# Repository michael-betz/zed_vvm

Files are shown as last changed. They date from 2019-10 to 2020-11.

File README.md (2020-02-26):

# zed_vvm
A digital RF vector volt-meter (VVM).
Measures amplitude and phase of a sinusoidal signal under test against a reference signal of same frequency.
Intended as an instrument to monitor and troubleshoot legacy accelerator RF systems.

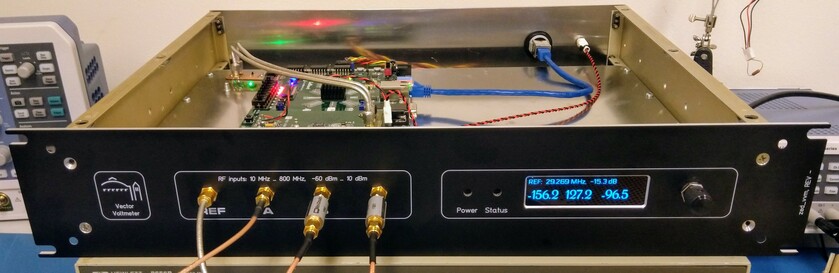
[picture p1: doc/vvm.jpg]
Photo of first prototype chassis


Based on a Digilent Zedboard running Debian with a DC1525A FMC daughter board on top.

  * 4 channel, 14 bit, 125 MSps, 800 MHz bandwidth (3 dB) analog to digital converter with LVDS interface: [__LTC2175-14__](https://www.analog.com/en/products/ltc2175-14.html)
  * Sampling clock provided by a `Si5xx-PROG_EVB` evaluation board running [custom firmware](https://github.com/yetifrisstlama/Si5xx-5x7-EVV_autoloader)
  * 4 x 4096 sample buffer with oscilloscope-like trigger for raw ADC waveform storage (`scope_app.py` makes use of that)
  * FPGA implements
    * digital down-conversion and decimation to get a complex baseband (IQ) signal
    * rectangular (IQ) to polar conversion (magnitude, phase)
    * first order IIR filter to smooth the measurement result
    * uses [Bedrock](https://github.com/BerkeleyLab/Bedrock) DSP blocks
    * makes good use of [litex](https://github.com/enjoy-digital/litex) Control/Status Registers (CSRs), the wishbone2axi bridge and litex_server to make the measurements available to linux running on the CPU

The main reason to choose embedded linux is the convenience for application development:
  * python3 support with numpy / scipy or even jupyter notebook
  * `sudo apt install <whatever_you_need>`
  * ssh and scp make remote access secure and easy, even on the public internet
  * remote loading of bit-files through scp is very convenient
  * litex_server can run on the zedboard, making access to CSR-registers over
    ethernet easy and transparent. The TCP connection is tunneled trough ssh,
    making it secure
  * can run epics IOC, mosquitto client or many other tools to publish
    measurement results

# Minimum design goals
  * support 125 MHz & 500 MHz signals
  * Same phase reading after power cycle (manage clock divider states)
  * 360 degree unique measurement range
  * Phase accuracy over a temperature range of 20 - 30 degC of better than 1 deg (0.2 %)
  * Less than 2 % amplitude error
  * At least 2 input channels + one phase reference channel
  * Self-contained instrument (only power is needed)
  * Easy to use
  * Not too expensive, such that it can be installed in multiple places across the facility
  * Epics support

# System block diagram
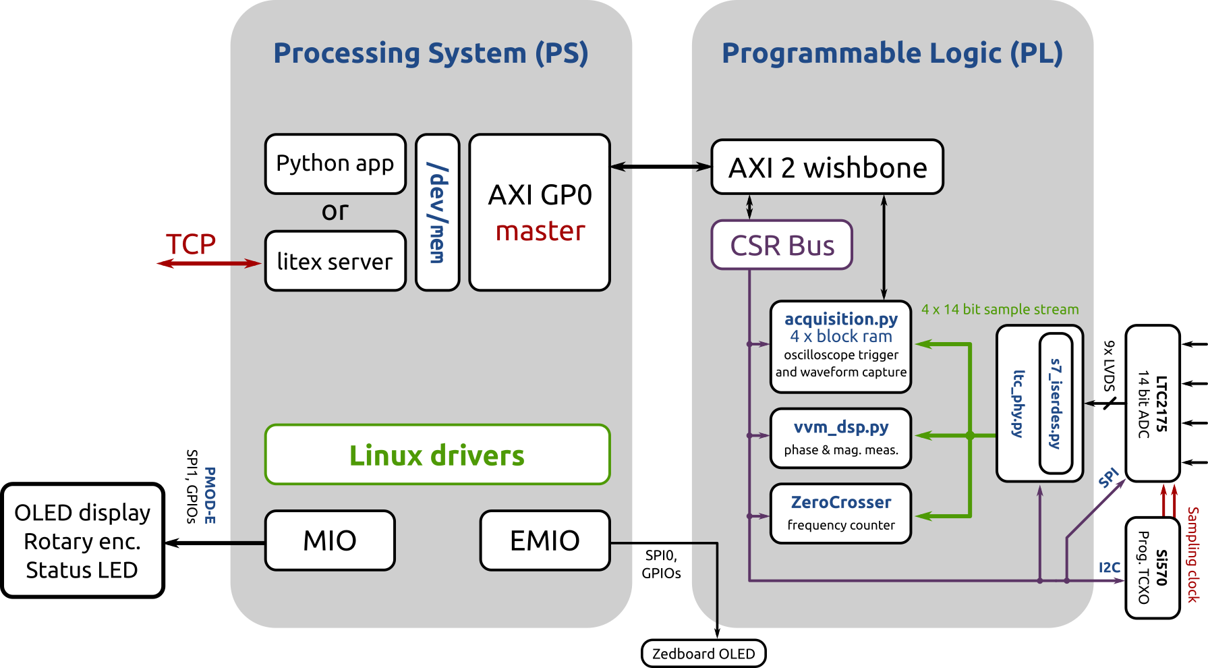
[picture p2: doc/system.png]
High level system overview


# `vvm_dsp.py` block diagram
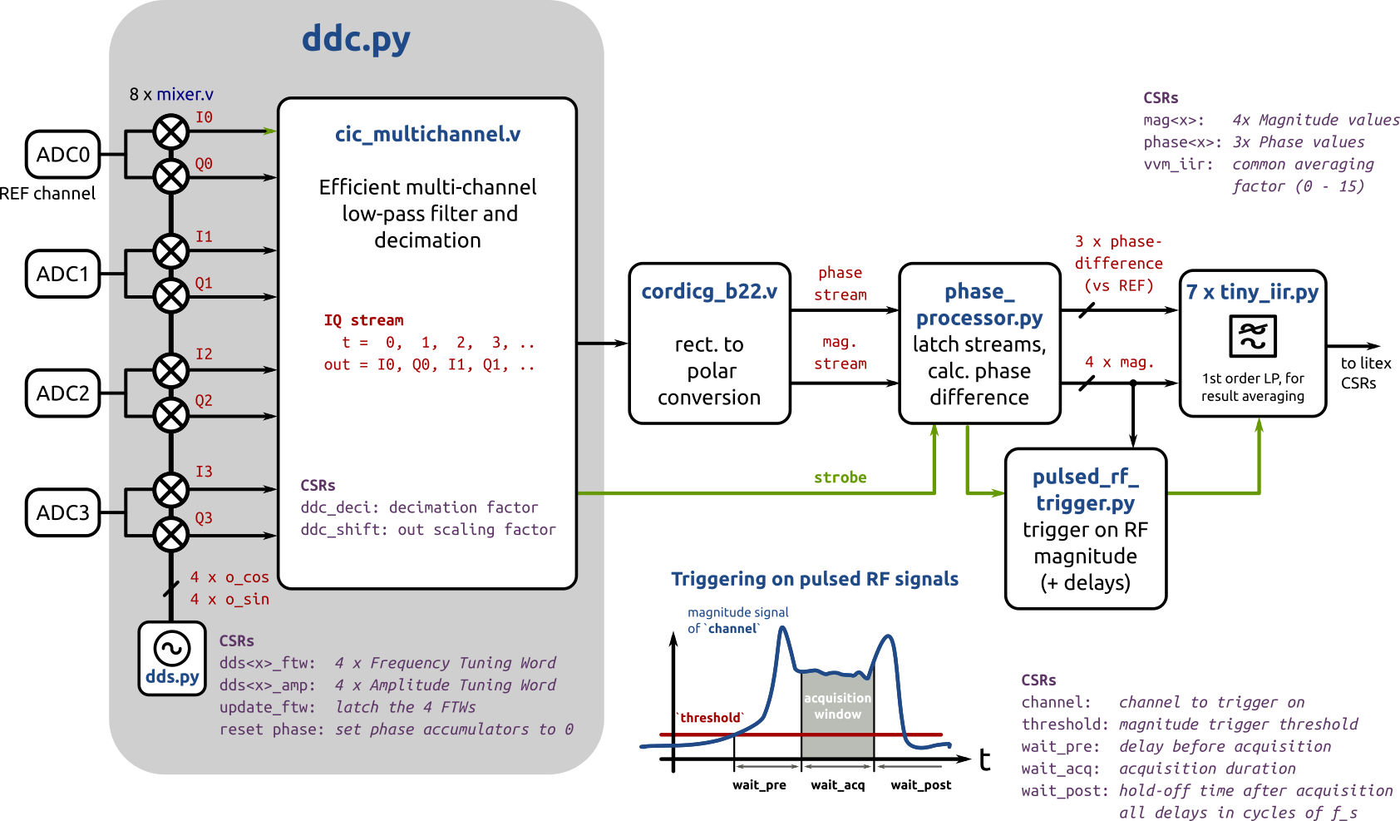
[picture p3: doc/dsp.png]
DSP blocks implementing the VVM


# `phase_processor.py` block diagram
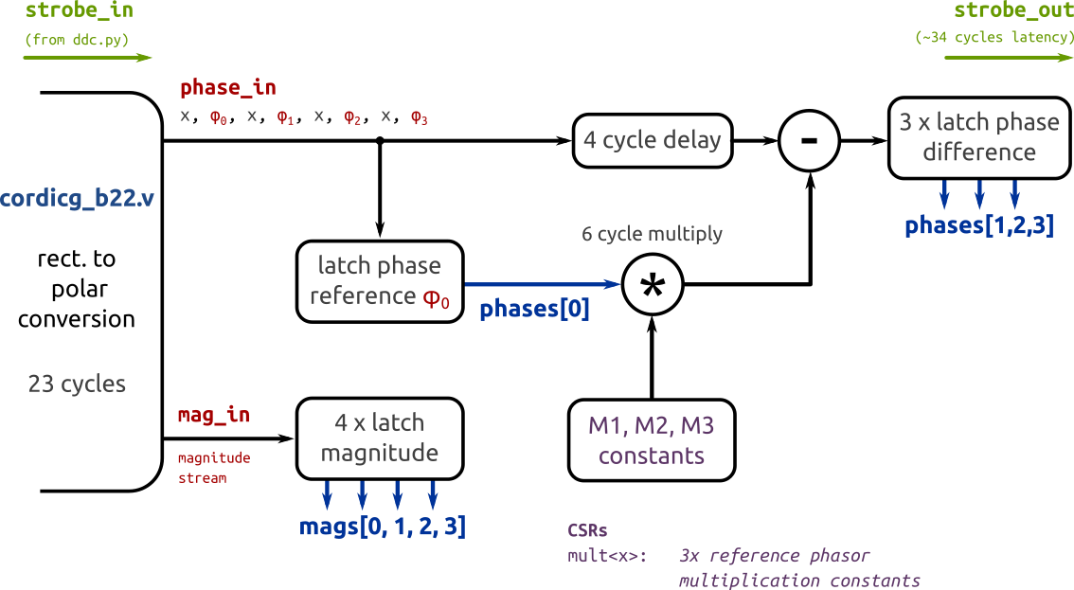
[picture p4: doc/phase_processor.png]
Phase and Magnitude pipelined data path


# Hardware modifications
## Zedboard
  * remove XADC header (J2) as it interferes with the DC1525A board

## DC1525A
  * Setup the board for differential sample clock input
    * Move R101 to R64 (0 Ohm jumper)
  * Remove low-pass filter on the analog input channels
    * Remove: R37, R38, R53, R54, R80, R81, R90, R91
    * Remove: R35, R52, R79, R89
    * Replace by 0 Ohm jumper: L4, L5, L6, L12

# Installing litex
... on debian
```bash
$ sudo apt install libevent-dev libjson-c-dev
$ sudo pip3 install virtualenvwrapper
$ mkvirtualenv litex
$ git clone git@github.com:yetifrisstlama/litex.git --recursive
$ cd litex
$ python litex_setup.py init
$ python litex_setup.py install
$ python setup.py develop
```

# Building the .bit file
Most of the DSP blocks are from LBLs `Bedrock` repo, which needs to be cloned
in the same directory as `zed_vvm`.

Vivado needs to be installed an in the PATH. I use v2019.1.

Setup your zedboard host-name in `util/remote_config_fpga.sh` and
`util/remote_litex_server.sh`.

Note that the Zedboard PS will freeze if the FPGA is not loaded / in the process of being loaded and there is a
AXI memory access through litex_server. So make sure to close the python apps before doing `make upload`.

```bash
$ git clone https://github.com/yetifrisstlama/zed_vvm.git
$ git clone https://github.com/BerkeleyLab/Bedrock.git
$ cd zed_vvm/gateware
$ workon litex
$ make
# remote FPGA configuration
$ make upload
# start litex_server on zedboard for remote access to FPGA registers
$ make server
# Keep this terminal open and start a new one
```

# Demo apps
[litex_server_apps](litex_server_apps/README.md)

# Setting up linux
[ZED_DEBIAN.md](linux_kernel/ZED_DEBIAN.md)

# Setting up Peripherals
How to connect Linux to the FPGA or the outside world. WIP ...

[PS_PERIPHERALS.md](linux_kernel/PS_PERIPHERALS.md)

# Load bitfile in linux
Bitfiles are loaded trough the [Linux FPGA Manager](https://www.kernel.org/doc/html/v4.18/driver-api/fpga/fpga-mgr.html).
For this to work, the .bit file needs its header removed and its bytes swapped.
This can either be done with the xilinx SDK or alternatively with `bitstream_fix.py`.
```bash
python3 util/bitstream_fix.py <bitfile>.bit
```

copy the resulting `<bitfile>.bit.bin` on the zedboard, then

```bash
    sudo -i
    cp <bitfile>.bit.bin /lib/firmware/
    echo 0 > /sys/class/fpga_manager/fpga0/flags
    echo <bitfile>.bit.bin > /sys/class/fpga_manager/fpga0/firmware
    dmesg

[ 1667.020520] fpga_manager fpga0: writing <bitfile>.bit.bin to Xilinx Zynq FPGA Manager
```

`cd gateware; make upload` tries to automate all these steps.

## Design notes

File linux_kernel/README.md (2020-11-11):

# linux_kernel

__.config__ my current mainline linux kernel configuration file for `make menuconfig`.
Copy / link it to `linux/.config`.

__zynq-zed.dts__ my current device tree.
Copy / link it to `linux/arch/arm/boot/dts/zynq-zed.dts`.

__fpga-mgr.patch__ Patch for the linux mainline kernel to get the /sys/class/fpga_mgr/fpga0/firmware file which is needed to easily configure the fpga from linux. The xilinx version of the kernel has this little convenience feature already builtin.

__ZED_DEBIAN.md__ Instructions on how to get a useful version of linux running on the zedboard.

__EPICS.md__ How to use `qemu` and `chroot` to cross-compile EPICS and an IOC and run it on the zedboard

__PS_PERIPHERALS.md__ Notes on how zynq peripherals are integrated into linux.

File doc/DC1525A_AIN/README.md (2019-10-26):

# LT spice simulation
... of the DC1525A analog input circuit.
It's a low-pass filter with corner frequency of ~ 100 MHz, made up of
discreet components.

As we want to measure 500 MHz signals, the low-pass needs to be removed.

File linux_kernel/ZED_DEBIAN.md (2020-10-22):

# Steps to get debian running on zedboard
It's like having a raspberry pi in your FPGA :)

This guide is mostly based on these two:
  * https://github.com/PyHDI/zynq-linux
  * https://blog.n621.de/2016/05/running-linux-on-a-zynq-without-vivado-madness/

## Bootloader
The stock version of U-Boot works perfectly fine for the Zynq7000 on the zedboard. No need for the Xilinx version.
```bash
# Cross compiler
    sudo apt install libc6-armel-cross libc6-dev-armel-cross binutils-arm-linux-gnueabi libncurses-dev
    sudo apt-get install gcc-arm-linux-gnueabi g++-arm-linux-gnueabi libssl-dev
    export CROSS_COMPILE=arm-linux-gnueabi-
    export ARCH=arm

# compile U-Boot
    git clone https://github.com/u-boot/u-boot.git
    cd u-boot/
    git checkout 0f3e2942c9e01b5dfc01f3dabe0e2f2ab8fd8b84
    export DEVICE_TREE=zynq-zed  # for zedboard
    make xilinx_zynq_virt_defconfig
    make menuconfig

# We want u-boot to read uEnv.txt from SD-card to setup its environment.
# Tick `Enable a default value for bootcmd`
# ... for `bootcmd value` enter the line below:
fatload mmc 0 0x10000 uEnv.txt;env import -t 0x10000 $filesize;boot

# Optional, apply a customized Zynq PS configuration on startup:
# under ARM architecture --> Zynq/ZynqMP PS init file(s) location
# enter:
<path to zed_vvm>/gateware/ip/ps7_init_gpl.c
# see also: `PS_PERIPHERALS.md`

    make

    # `mkimage` will be needed for building the kernel
    export PATH=$PATH:<..>/u-boot/tools/

# Create a ~ 64 MB FAT32 partition on the SD card,
# follow the guide below or use gparted
# in this example it's mounted as /media/sdcard

# Copy first stage bootloader and u-boot image to SD card
    cp spl/boot.bin /media/sdcard
    cp u-boot.img /media/sdcard

# Now try it on the Zedboard, you should see u-boot starting on the UART
```
### Erasing the flash
There's a caveat here. U-Boot can store its environment in the SPI flash, which will override the default $bootcmd we set up in menuconfig. To fix this, erase the flash from within the u-boot shell:

```bash
# This is a sign that uEnv.txt was not loaded correctly from MMC
Zynq> echo $bootcmd
run $modeboot

# Flash needs to be erased ...
Zynq> sf probe
Zynq> sf erase 0 0x2000000
Zynq> reset

# Now it looks good:
Zynq> echo $bootcmd
run kernel_load; run dtr_load; setenv ethaddr 00:0a:35:00:01:87; run kernel_boot
```

### bootstrapping u-boot over JTAG
... with openocd
```tcl
reset halt
load_image u-boot/spl/u-boot-spl.bin 0
resume 0
sleep 1000
halt
load_image u-boot/u-boot.bin 0x4000000
resume 0x4000000
```

### Installing u-boot to flash
https://xilinx-wiki.atlassian.net/wiki/spaces/A/pages/18842574/U-Boot+Secondary+Program+Loader

## Linux kernel
The [vanilla mainline kernel](https://github.com/torvalds/linux) works perfectly fine on the zedboard for this application (see note below).
Here's instructions on how to apply two tiny patches to enable FPGA configuration from the command line and OLED support. If you go with the Xilinx version of the kernel, you don't need the two patches, but most of the instructions below still apply.

```bash
    git clone https://github.com/torvalds/linux.git
    cd linux/
    git checkout 22fbc037cd32e4e6771d2271b565806cfb8c134c

# Load my kernel config and device tree for zed_vvm
    cp <..>/zed_vvm/linux_kernel/zedboard_defconfig arch/arm/configs/
    cp <..>/zed_vvm/linux_kernel/zynq-zed.dts arch/arm/boot/dts/

# Patch to get /sys/class/fpga_mgr/fpga0/firmware
# Not needed with the xilinx version of the kernel
    patch --strip=1 --input=<..>/zed_vvm/linux_kernel/fpga-mgr.patch

# If you want to use the tiny ssd1306 based display on the zed-board,
# replace the kernel fbtft driver with a working version:
    cd drivers/staging
    rm -rf fbtft
    git clone https://github.com/yetifrisstlama/fbtft.git

# Apply any kernel customization you might need
    cd ../..
    export CROSS_COMPILE=arm-linux-gnueabi- ARCH=arm
    make zedboard_defconfig
    make menuconfig
    # make sure the display drivers are all enabled under
    # Device Drivers --> Staging drivers --> Support for small TFT LCD display modules
```

Then build the kernel and device-tree ...

```bash
    make -j4 uImage LOADADDR=0x00008000
    # good time to get a cup of coffee
    make zynq-zed.dtb
```

copy kernel image and device-tree to SD card

```bash
    cp arch/arm/boot/uImage /media/sdcard/
# for zedboard
    cp arch/arm/boot/dts/zynq-zed.dtb /media/sdcard
# for microzed
    cp arch/arm/boot/dts/zynq-microzed.dtb /media/sdcard
```

to configure u-boot, create a `uEnv.txt` as shown below and copy it to SD card.

SD card contents should look like this now:
```bash
ls -hl /media/<..>
total 5.6M
-rw-r--r-- 1 michael michael 117K Oct  3 19:42 boot.bin
-rw-r--r-- 1 michael michael 1.1M Oct  3 19:42 u-boot.img
-rw-r--r-- 1 michael michael  735 Oct  3 19:42 uEnv.txt
-rw-r--r-- 1 michael michael 4.4M Oct  3 19:43 uImage
-rw-r--r-- 1 michael michael  12K Oct  3 19:43 zynq-zed.dtb
```
Now is a good time to give it a test-run on the Zedboard,
the linux kernel should boot and panic because of the missing root filesystem

## Mainline kernel
Pros of going mainline
  * more widely adopted
  * hence better peer-reviewed

The Zynq7000 is pretty well supported now in the mainline kernel.

[Mainline vs. Xilinx Kernel](https://xilinx-wiki.atlassian.net/wiki/spaces/A/pages/18841873/Linux+Drivers)

I started this project on the Xilinx kernel-fork. When I first tried switching over to mainline, I just copied `linux-xlnx/.config` to `linux/.config` and compiled as of the instructions above.

  * Both OLED displays, GPIOs and rotary encoder worked as expected
  * It booted without errors in dmesg
  * `/sys/class/fpga_manager/fpga0` was there, so the linux FPGA manager driver was working

However I was missing `/sys/class/fpga_manager/fpga0/firmware`,
which is used to pipe the name of a `.bit.bin` file to re-program the FPGA PL from linux. After some investigation, it looks like the fpga-manager was not intended to be accessed from user-space and Xilinx added this feature as a convenience for developers. I brought it back with a [tiny patch](fpga-mgr.patch) to the mainline kernel.

With the patch I was able to load bit-files in the same way as with the
 Xilinx kernel. However the fabric clocks were still disabled and the FPGA
 appeared completely un-responsive after configuration.
 Some intensive diff-ing later I could trace this down to different default settings in `zynq-7000.dtsi`.
 Switching the clocks back on was easily done in [`zynq-zed.dts`](zynq-zed.dts)
 and life on mainline is good now.

## Debian buster rootfs

### Shortcut: install pre-made rootfs
This assumes `/dev/mmcblk0p2` is the large ext4 partition on the SD card/.
```bash
    wget https://github.com/yetifrisstlama/zed_vvm/releases/download/v0.1/rootfs_buster_clean.tar.gz
    sudo mkfs.ext4 -v /dev/mmcblk0p2 -L rootfs
    # Mount the partition (easiest in gui file manger)
    cd /media/<..>/rootfs
    sudo tar -xzvf <..>/rootfs_buster_clean.tar.gz
    sync
```

Put the SD-card in the zedboard, connect to its UART and
watch it booting into debian. There should be a login prompt on the UART.

__If you've downloaded `rootfs_buster_clean.tar.gz` change the passwords !!!__
login as each of the two users below and run the `passwd` command.

```bash
    #user: root, default pw: root
    #user: zed, default pw: zed
```

Also remote login over ssh should work now if the network is up.

The last step (if ssh works) is to copy the `linux_apps` directory
form the host machine onto the zedboard:

```bash
    scp -r <..>/zed_vvm/linux_apps <user_name>@<hostname>:~
```

Alternatively, just install my [litex-fork](https://github.com/yetifrisstlama/litex) on the zedboard, which includes
litex_server with mmap access support.

### Debian certificate troubles
I forgot to include openssl in `rootfs_buster_clean.tar.gz`. So `sudo apt update` may refuse to work and complain about missing certificates. I fixed this by downloading on my host machine:

  * [openssl-armhf](https://packages.debian.org/buster/openssl)
  * [ca-certificates](https://packages.debian.org/buster/ca-certificates)

copying them on the zeboard with `scp` and installing them with `sudo apt install ./<file_name>`.

### Taking the scenic route ...
setup your initial bare-bones debian environment using chroot on a debian based linux host PC.

```bash
# debian rootfs (on host)
    sudo apt install debootstrap qemu-user-static
    mkdir rootfs
    sudo debootstrap --arch=armhf --foreign buster rootfs
    sudo cp /usr/bin/qemu-arm-static rootfs/usr/bin/
    sudo chroot rootfs/

# debian rootfs (chroot)
    distro=buster
    export LANG=C
    debootstrap/debootstrap --second-stage
    nano /etc/apt/sources.list

deb http://deb.debian.org/debian buster main
deb http://deb.debian.org/debian-security/ buster/updates main
deb http://deb.debian.org/debian buster-updates main

    apt update
    apt upgrade
    apt install locales sudo ntp openssh-server python3

    # Enable `en_US.UTF-8` and set it as default locale
    dpkg-reconfigure locales

    # Set root password
    passwd

    # Add a user with sudo permissions
    adduser <user_name>
    visudo

root        ALL=(ALL:ALL) ALL
<user_name> ALL=(ALL:ALL) NOPASSWD: ALL
# Note: the `NOPASSWD: ` flag means sudo will not ask for a password.
# convenient for development but dangerous. Don't do this in production!

    # Enable DHCP
    nano /etc/network/interfaces

allow-hotplug eth0
iface eth0 inet dhcp

    # Set hostname
    nano /etc/hostname

<hostname>

    nano /etc/hosts

127.0.0.1   localhost <hostname>
::1     localhost ip6-localhost ip6-loopback
ff02::1     ip6-allnodes
ff02::2     ip6-allrouters

# Mount the fat16 boot partition
# This is useful for remote updates of
#   * first stage boot-loader (boot.bin)
#   * u-boot.img
#   * device tree (.dts)
#   * kernel image (uImage)
#   * u-boot config (uEnv.txt)
    mkdir /boot  # only if it does not exist already
    nano /etc/fstab

/dev/mmcblk0p1 /boot auto defaults 0 0

# For remote fpga loading
    mkdir /lib/firmware

# Optional Hacks
# get cross-compiled binaries to run
# otherwise I get `bash: ./hw: No such file or directory`
    sudo ln -s /lib/arm-linux-gnueabihf/ld-2.28.so /lib/ld-linux.so.3

# to prevent sshd taking forever to start after reboot and
# `random: 7 urandom warning(s) missed due to ratelimiting`
    sudo apt install haveged

# ------------------------
#  Exit the chroot shell
# ------------------------

# Archive rootfs in a .tar.gz file
    cd rootfs
    sudo tar -cpzvf ../rootfs_buster_clean.tar.gz .
```

Un-tar the rootfs onto a large ext4 partition on the SD card as shown [here](ZED_DEBIAN.md#shortcut-install-pre-made-rootfs).

## Partitioning the SD card
What we need

  * FAT16 partition of size 32 MB
  * Linux (ext4) over the remaining available space

Using `fdisk` on a 2 GB SD card, it should look like this:

```
Device         Boot Start     End Sectors  Size Id Type
/dev/mmcblk0p1       2048   67583   65536   32M  e W95 FAT16
/dev/mmcblk0p2      67584 3842047 3774464  1.8G 83 Linux
```

then format the partitions as FAT16 and ext4

```bash
sudo mkfs.vfat -F16 -v /dev/mmcblk0p1 -n boot
sudo mkfs.ext4 -v /dev/mmcblk0p2 -L rootfs
```

__make sure to replace `mmcblk0p1` and `mmcblk0p2` with the actual partition names__

# uEnv.txt
U-Boot startup script to boot and optionally load a bitfile. Make sure `ethaddr` is unique on network.
```bash
# I get corrupt data from MMC if the caches are enabled :(
init=icache off; dcache off

fpga_addr=0x10000000
fpga_load=load mmc 0 ${fpga_addr} zed_wrapper.bit.bin
fpga_boot=fpga load 0 ${fpga_addr} $filesize

kernel_addr=0x8000
kernel_load=load mmc 0 ${kernel_addr} uImage

dtr_addr=0x100
dtr_load=load mmc 0 ${dtr_addr} zynq-zed.dtb

kernel_boot=setenv bootargs console=ttyPS0,115200 root=/dev/mmcblk0p2 rw rootwait; bootm ${kernel_addr} - ${dtr_addr}

# Boot from MMC without loading a bit-file, make sure to change ethaddr to a random value
bootcmd=run init; run kernel_load; run dtr_load; setenv ethaddr 00:0a:35:00:42:87; run kernel_boot

# Load a bit-file and boot from MMC, make sure .bit.bin file from line 2 exists
# bootcmd=run init; run fpga_load; run fpga_boot; run kernel_load; run dtr_load; setenv ethaddr 00:0a:35:00:42:87; run kernel_boot

# network boot: load uImage and zynq-zed.dtb over tftp and boot it
# ipaddr=192.168.1.2
# serverip=192.168.1.1
# netmask=255.255.255.0
# bootcmd=run init; tftpboot $kernel_addr uImage; tftpboot $dtr_addr zynq-zed.dtb; run kernel_boot
```

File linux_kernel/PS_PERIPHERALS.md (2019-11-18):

# PS7 peripherals configuration
The Zynq Processing System (PS) is the CPU part of the FPGA. It has several peripherals like SPI, CAN, I2C, UART, GPIO, etc. These are connected to dedicated IO pins on the chip (MIO) or to the FPGA Programmable Logic (EMIO), from where they can be routed to any other IO pin of the chip through the FPGA fabric. Configuration happens in Vivado through the `ZYNQ7 Processing system` IP block.

If the PS7 block is not included in the PL design, the CPU will freeze as soon as the the resulting bitfile is loaded. The PL part of the design will work as intended, even without the PS7 block.

Configuration of the PS7 block is stored in the Xilinx IP file `ip/processing_system7_0.xci`, which is required by the Litex `SoCZynq()` class.

To manually generate this file, follow these steps:

  1. open Vivado, new RTL project, `zedboard` hardware platform, don't add source files, next, next next ..
  2. IP Integrator --> Create Block Design
  3. Add `ZYNQ7 Processing system` IP
  4. Run vivado design automation to get default values for Zedboard
  5. Configure the PS7 block in GUI
       * Bank0 / 1 voltage = 2.5 V
       * Clock Configuration, PL Fabric Clocks: clock0 100 MHz. The litex `sysclk` domain is driven by clock0
  6. Peripheral I/O Pins
       * The PS_MIOX pins are connected to the PS and can be configured here for special function operation (like CAN, I2C, SPI, UART, GPIO)
       * PMOD JE1 is exclusively connected to MIOs (see table below). This might be useful to drive a small graphical LCD from linux trough an SPI interface
  7. Save and close, this generates the file `<name>.srcs/sources_1/ip/processing_system7_0/processing_system7_0.xci` in the project directory, which needs to be copied to `./ip`

__All these steps have now been automated by `ip/gen_ip.tcl`.__

This .tcl script is automatically run by the Makefile. If you want to change the PS configuration, change only this file.

## Peripherals connected to PS

These are accessible from linux when configured in step 6 above (most are already configured by default) and once the right driver has been loaded, which requires an entry into the linux device tree.

| Net      |PS_EMIO<x> |              |
| -------- | --------- | ------------ |
|__PMOD-A__|           | __FP PCB__   |
|  JA1     | 54        | ENCODER: B   |
|  JA2     | 55        | ENCODER: SW  |
|  JA3     | 56        | ENCODER: A   |
|  JA4     | 57        | STATUS_LED   |
| JA10     |           | OLED: MOSI   |
|  JA9     |           | OLED: SCLK   |
|  JA8     |           | OLED: /CS    |
|  JA7     | 58        | OLED: D/C    |
|__PMOD-B__|           |__Si570 PCB__ |
|  JB1     |           |              |
|  JB2     |           |              |
|  JB3     |           |              |
|  JB4     |           |              |
| JB10     |           | SDA          |
|  JB9     |           | SCL          |
|  JB8     |           | OE           |
|  JB7     |           | NC           |

### PMOD-E is dedicated to the PS-wired MIO pins
Will be used with the front panel PCB for the user interface.

| Net      | PS_MIO<x> | PS7, SPI1  |              |
| -------- | --------- | ---------- | ------------ |
|__PMOD-E__|           |            | __FP PCB__   |
|  JE1     | 13        | SS[0]      | OLED: /CS    |
|  JE2     | 10        | MOSI       | OLED: MOSI   |
|  JE3     | 11        | MISO       | ENCODER: SW  |
|  JE4     | 12        | SCLK       | OLED: SCLK   |
| JE10     | 15        | SS[2]      | OLED: D/C    |
|  JE9     | 14        | SS[1]      | STATUS_LED   |
|  JE8     | 9         |            | ENCODER: B   |
|  JE7     | 0         |            | ENCODER: A   |
|__Button__|           |            |              |
|  PB1     | 50        |            |              |
|  PB2     | 51        |            |              |
| __LED__  |           |            |              |
|  LD9     |7 (USB rst)|            |              |

Note on PS7:
  * MIO0 - MIO53
  * EMIO54 - EMIO117

Change MIO11 from MISO to GPIO with pullup in `ps7_init_gpl.c`.
The Vivado GUI does not allow this configuration, that's why we have
to hack it.

```
    from: EMIT_MASKWRITE(0XF800072C, 0x00003FFFU ,0x000007A0U),
    to:   EMIT_MASKWRITE(0XF800072C, 0x00003FFFU ,0x00001600U)
```
this has been automated in the Makefile

# Zedboard OLED
TODO: add guide to get FBTFT running

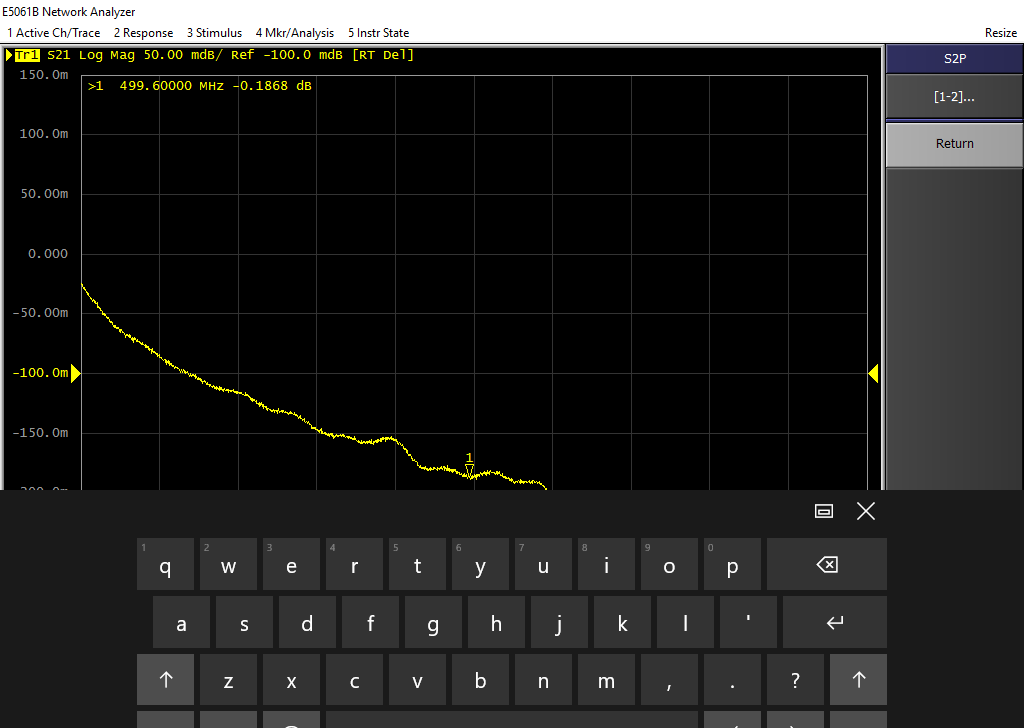
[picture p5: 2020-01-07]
litex_server_apps/cal/vna/CAB.PNG

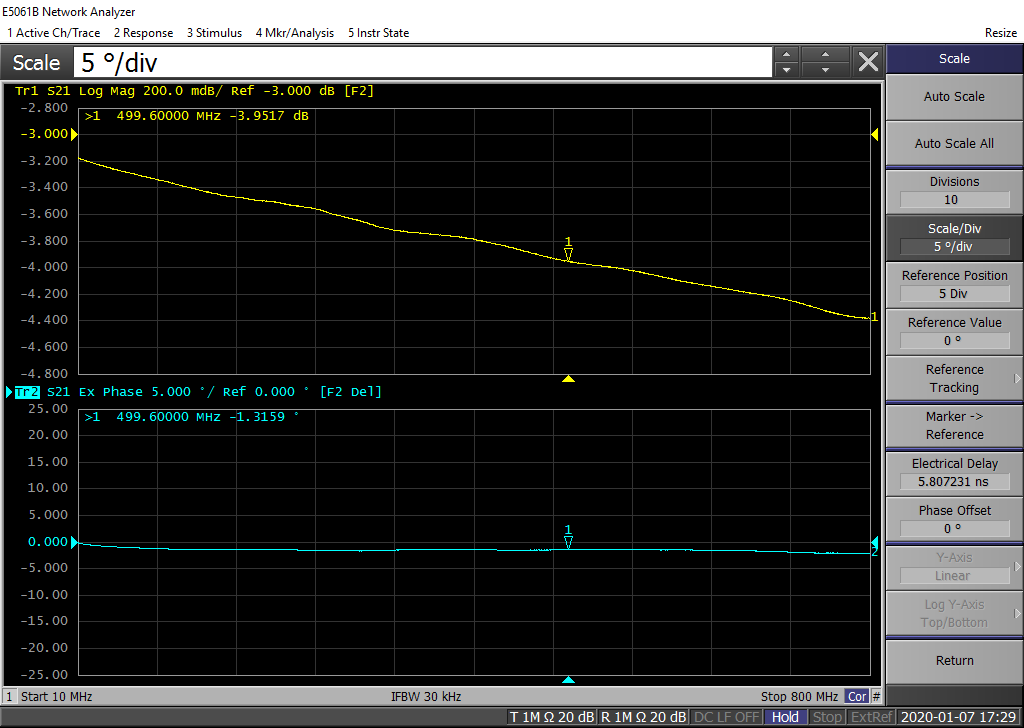
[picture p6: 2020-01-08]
litex_server_apps/cal/vna/PDIV_CH1.PNG

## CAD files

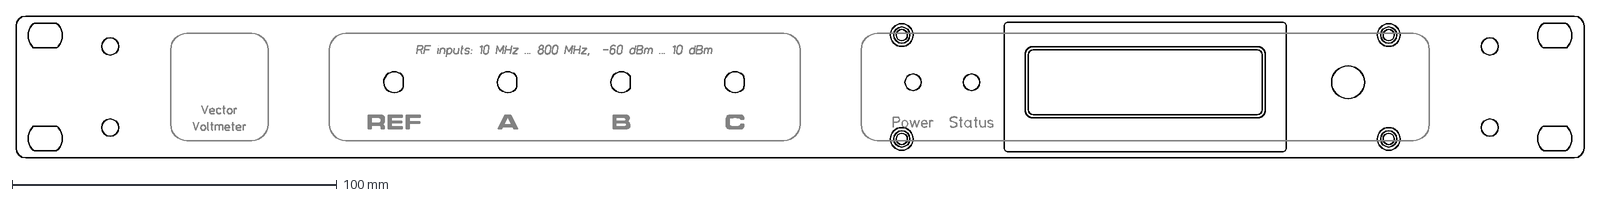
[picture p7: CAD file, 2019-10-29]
pcb/frontpanel/vvm.dxf
483.0 x 43.6 mm

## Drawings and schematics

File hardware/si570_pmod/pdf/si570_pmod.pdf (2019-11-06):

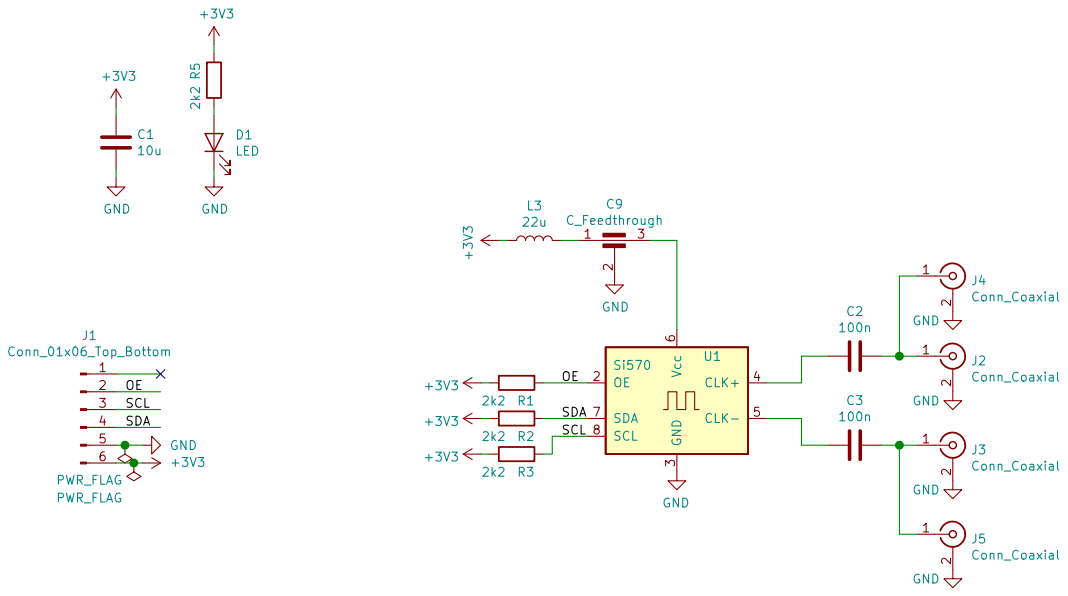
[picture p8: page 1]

3 CLK+ 4 CLK- 5 Vcc 6 SDA 7 SCL 8 U1
SCL SDA OE

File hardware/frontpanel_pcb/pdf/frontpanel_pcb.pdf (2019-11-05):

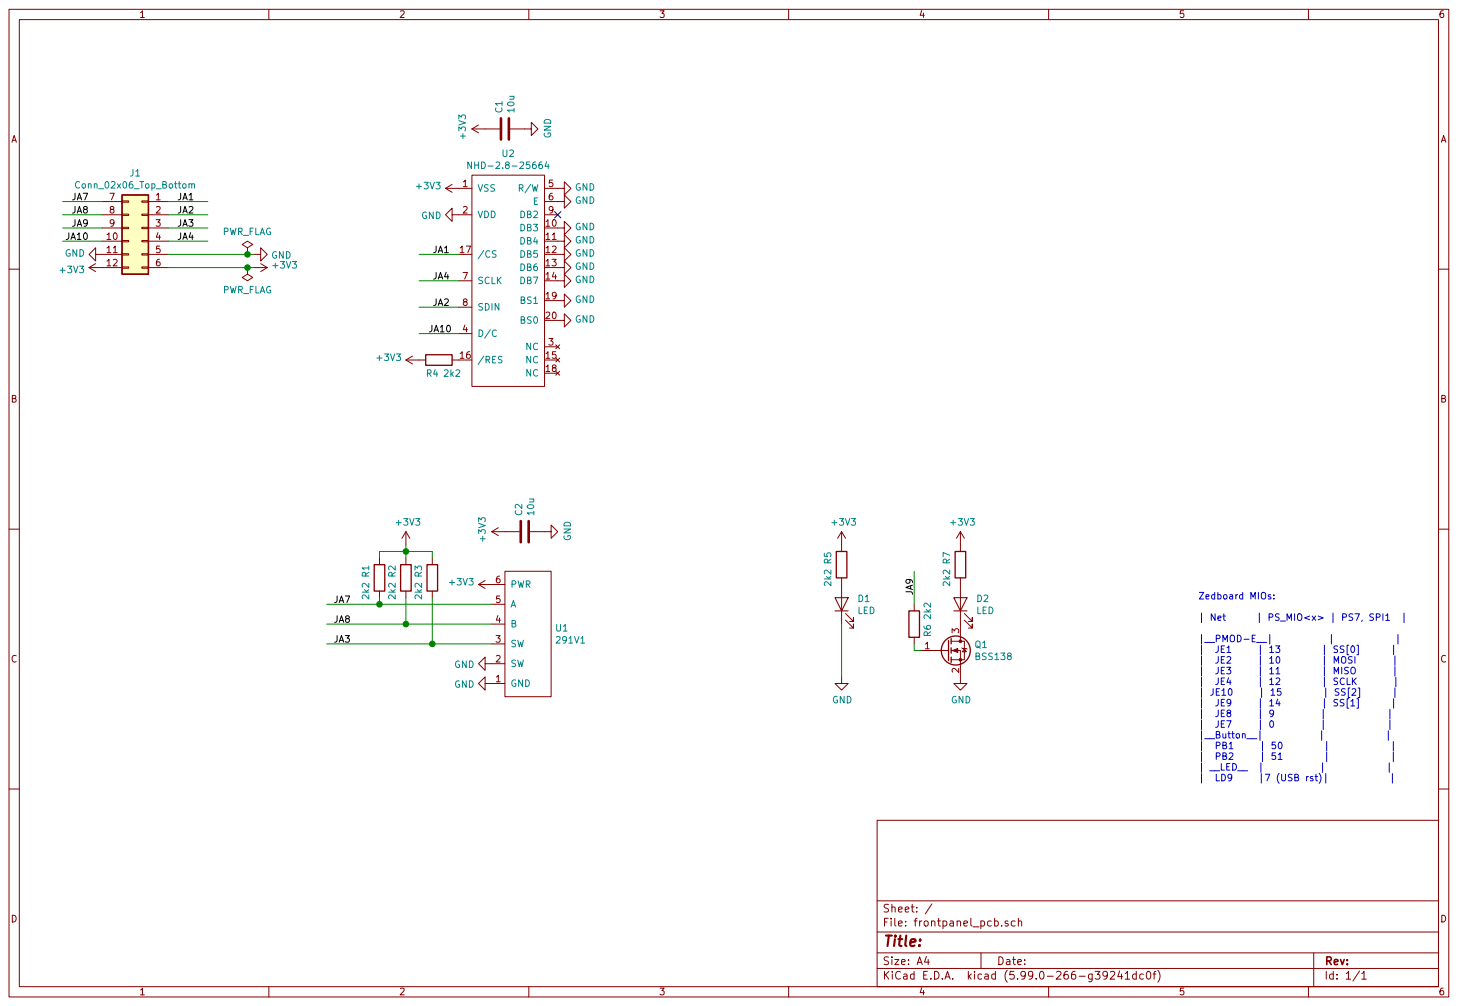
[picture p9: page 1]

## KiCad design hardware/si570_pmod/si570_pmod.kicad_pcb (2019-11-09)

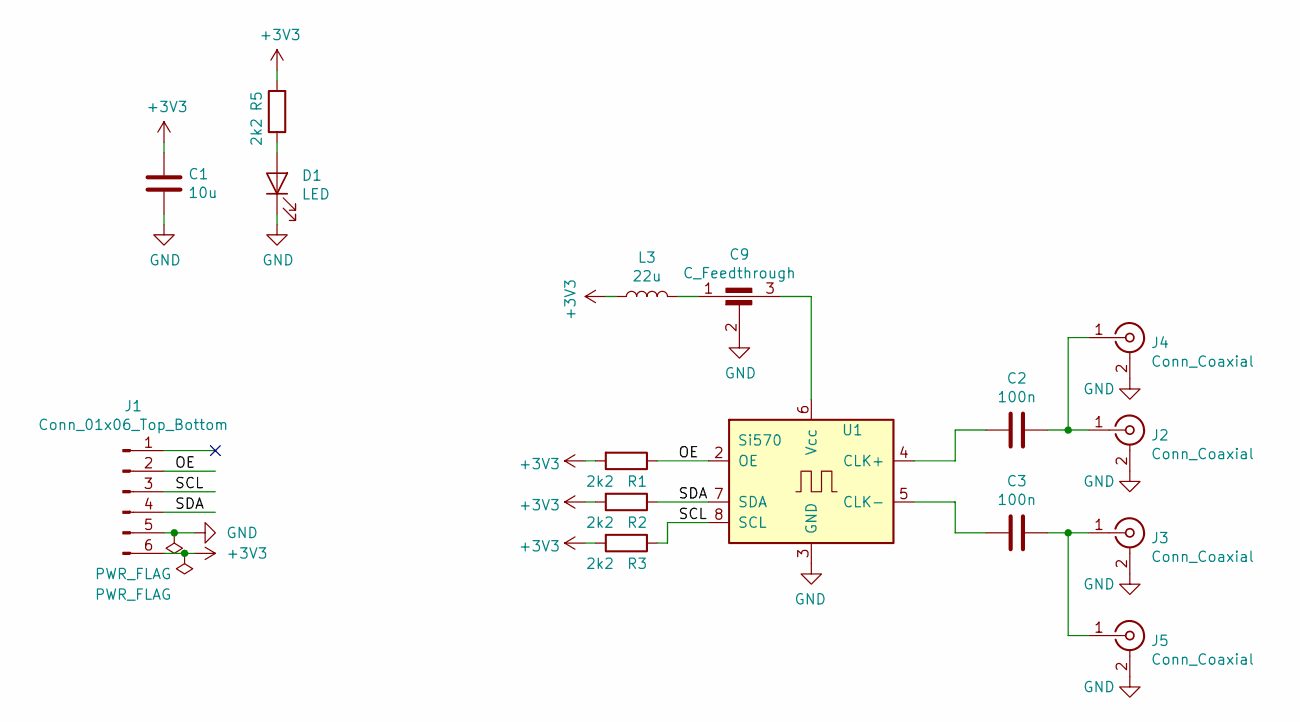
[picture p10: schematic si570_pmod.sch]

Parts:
C1: 10u; C_1206_3216Metric
C2, C3: 100n; C_0805_2012Metric
C9: C_Feedthrough; NFM31PC
D1: LED; LED_0805_2012Metric
J1: Conn_01x06_Top_Bottom; PinHeader_1x06_P2.54mm_Horizontal
J2, J3: Conn_Coaxial; SMA_Amphenol_132289_EdgeMount
J4, J5: Conn_Coaxial; SMA_Amphenol_132134-11_Vertical
L3: 22u; L_1210_3225Metric
R1, R2, R3, R5: 2k2; R_0805_2012Metric
U1: Si570; Oscillator_SMD_SI570_SI571_Standard

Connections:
+3V3: C1.1, J1.6, L3.1, R1.2, R2.2, R3.2, R5.2
/OE: J1.2, R1.1, U1.2 (OE)
/SCL: J1.3, R3.1, U1.8 (SCL)
/SDA: J1.4, R2.1, U1.7 (SDA)
GND: C1.2, C9.2, D1.1 (K), J1.5, J2.2 (Ext), J3.2 (Ext), J4.2 (Ext), J5.2 (Ext), U1.3 (GND)
unnamed: C2.1, J2.1 (In), J4.1 (In)
unnamed: C2.2, U1.4 (CLK+)
unnamed: C3.1, J3.1 (In), J5.1 (In)
unnamed: C3.2, U1.5 (CLK-)
unnamed: C9.1, L3.2
unnamed: C9.3, U1.6 (Vcc)
unnamed: D1.2 (A), R5.1

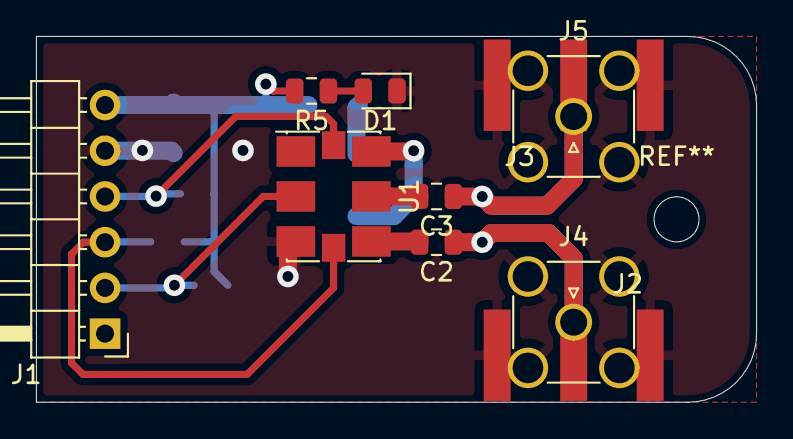
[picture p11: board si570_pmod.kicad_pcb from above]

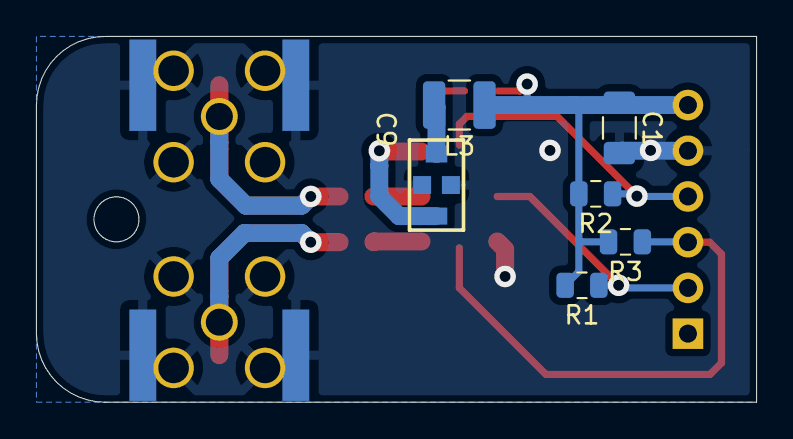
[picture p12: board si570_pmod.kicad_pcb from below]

Board: 2 copper layers, 40.0 x 20.3 mm, 16 parts (6 on the bottom side), 12 nets.

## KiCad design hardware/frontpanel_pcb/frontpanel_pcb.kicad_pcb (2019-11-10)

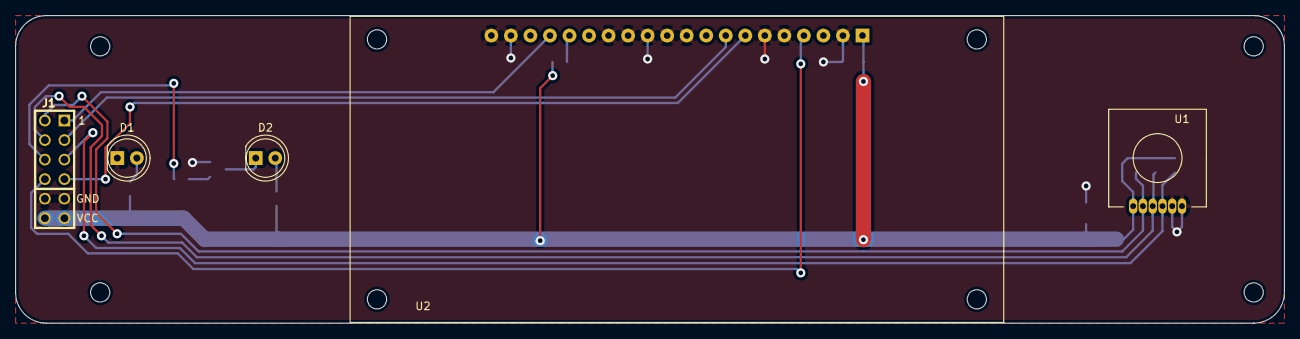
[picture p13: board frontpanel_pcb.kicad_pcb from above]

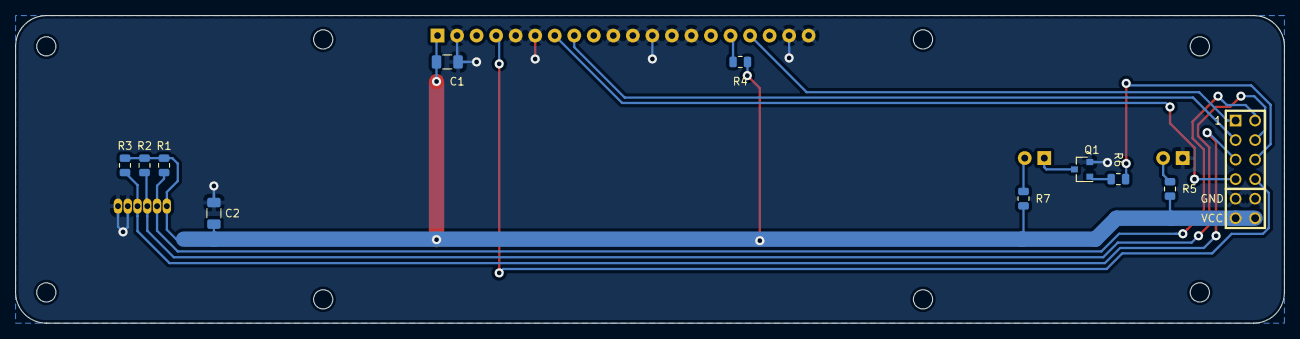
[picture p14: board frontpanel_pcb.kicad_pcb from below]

Board: 2 copper layers, 165.0 x 40.0 mm, 15 parts (10 on the bottom side), 15 nets.

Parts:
C1, C2: 10u; C_1206_3216Metric
D1, D2: LED; LED_D5.0mm
J1: Conn_02x06_Top_Bottom; pmod_pin_array_6x2
Q1: BSS138; SOT-23
R1, R2, R3, R4, R5, R6, R7: 2k2; R_0805_2012Metric
U1: 291V1
U2: NHD-2.8-25664; NHD-2.8-25664UCB2

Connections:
+3V3: C1.1, C2.1, J1.6, J1.12, R1.2, R2.2, R3.2, R4.2, R5.2, R7.2, U1.6, U2.1
/JA1: J1.1, U2.17
/JA2: J1.2, U2.8
/JA3: J1.3, R3.1, U1.3
/JA4: J1.4, U2.7
/JA7: J1.7, R1.1, U1.5
/JA8: J1.8, R2.1, U1.4
/JA9: J1.9, R6.1
/JA10: J1.10, U2.4
GND: C1.2, C2.2, D1.1, J1.5, J1.11, Q1.2, U1.1, U1.2, U2.2, U2.5, U2.6, U2.10, U2.11, U2.12, U2.13, U2.14, U2.19, U2.20
unnamed: D1.2, R5.1
unnamed: D2.1, Q1.3
unnamed: D2.2, R7.1
unnamed: Q1.1, R6.2
unnamed: R4.1, U2.16

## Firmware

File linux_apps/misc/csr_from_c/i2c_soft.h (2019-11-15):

//-------------------------------------------------
// I2C bit-bang library
//-------------------------------------------------
// Expects the following macros in settings.h:
// #define PIN_I2C_SDA              0  // GPIO pin number of the data pin
// #define PIN_I2C_SCL              1  // GPIO pin number of the clock pin
// #define I2C_DELAY_US             1  //~half a clock period [us]
// #define BASE_GPIO       0x01000000  //base address of the gpio module used for soft_i2c

#ifndef I2C_SOFT_H
#define I2C_SOFT_H

#include <stdint.h>

#define I2C_R                1
#define I2C_W                0
#define I2C_ACK              1
#define I2C_NACK             0

//-------------------------------------------------
// Low level functions (doing I2C things)
//-------------------------------------------------
void i2c_init(void);                // initialize GPIO pins
void i2c_stop(void);                // Send I2C start-condition
void i2c_start(void);               // Send I2C stop-condition
int i2c_tx( uint8_t dat );  // sends out 8 bits (dat), returns ack (9th bit, 1 = ack ok)
uint8_t i2c_rx( int ack );  // reads & returns 8 bit, sends ack

//-------------------------------------------------
// High level functions (dealing with registers)
//-------------------------------------------------
// Typical register based writing (write regAddr, then write data)
// i2cAddr = 7 bit I2C address. MSB = 0.
// returns 1 on success, 0 if one or more ACK bits were missing
int i2c_write_regs( uint8_t i2cAddr, uint8_t regAddr, uint8_t *buffer, uint16_t len );
int i2c_write_reg(uint8_t i2cAddr, uint8_t regAddr, uint8_t val);

// Typical register based reading (write regAddr, then read data)
// i2cAddr = 7 bit I2C address. MSB = 0.
// returns 1 on success, 0 if one or more ACK bits were missing
int i2c_read_regs( uint8_t i2cAddr, uint8_t regAddr, uint8_t *buffer, uint16_t len );

//-------------------------------------------------
// Debugging functions (printing stuff)
//-------------------------------------------------
// Scan through all I2C addresses, try to write and
// reports the ones which respond with an ack
void i2c_scan(void);

// Read data over I2C and print it as a hex-dump to UART
// i2cAddr= 7 bit i2c slave address
// regAddr= register offset
// nBytes = number of bytes to read
int i2c_dump( uint8_t i2cAddr, uint8_t regAddr, int nBytes );

// Read data over I2C and directly print it as characters to UART
// adr    = 7 bit i2c slave address
// regAddr= register offset
// nBytes = number of bytes to read
int i2c_read_ascii( uint8_t i2cAddr, uint8_t regAddr, int nBytes );

#endif

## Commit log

2019-10-29 add inital draft of front-panel and pcb
    [frontpanel_pcb.kicad_pcb, frontpanel_pcb.sch, vvm.dxf]
2019-10-30 First PCB cut
    [frontpanel_pcb-B_Cu.gbr, frontpanel_pcb-Edge_Cuts.gbr, frontpanel_pcb-F_Cu.gbr, frontpanel_pcb.drl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]
2019-10-30 directory cleanup
    [frontpanel_pcb-B_Cu.gbr, frontpanel_pcb-Edge_Cuts.gbr, frontpanel_pcb-F_Cu.gbr, frontpanel_pcb.drl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]
2019-10-30 simplified pullups
    [frontpanel_pcb.kicad_pcb]
2019-10-31 Streamlined .xci IP generation
    [frontpanel_pcb.sch]
2019-11-01 frontpanel_pcb.sch: revert to pin-out as milled
    [frontpanel_pcb.sch]
2019-11-01 fix PMODA pin-out
2019-11-05 hardware: add 2U front / back panel, add Si570 board
    [frontpanel_pcb.sch, si570_pmod.kicad_pcb, si570_pmod.sch]
2019-11-05 Fix display board PMOD pinout
    [frontpanel_pcb.kicad_pcb, frontpanel_pcb.sch]
2019-11-05 frontpanel: update to metric, remove outdated
    [frontpanel_pcb.kicad_pcb, vvm.dxf]
2019-11-05 Move a via out of the way
    [frontpanel_pcb.kicad_pcb]
2019-11-06 fine-tune PCBs and FP, ordered first hardware
    [si570_pmod.kicad_pcb, si570_pmod.sch]
2019-11-06 si570_pmod: make SMA footprint milling compatible
    [si570_pmod.kicad_pcb]
2019-11-08 Update u-boot instruictions
    [si570_pmod.kicad_pcb]
2019-11-09 pmod si570: add note about flipped J1
    [si570_pmod.kicad_pcb]
2019-11-10 frontpanel_pcb: change mounting holes to 2.5 mm
    [frontpanel_pcb.kicad_pcb]
2019-11-16 Rotary encoder and OLED works!
    [frontpanel_pcb.sch]
2019-11-20 cleanup common.py, add led to .dts
    * make csr_access compatible with litex_client (adapter class)
    * move stuff from common.py to vvm_helpers.py
    * add status led to device tree and kernel config
    * fix scope_app (Si570 setup doesnt work through litex_server)
2020-01-07 first stab at magnitude calibration over f
2020-01-07 Improve magnitude calibration
    something's wrong with channel 0 magnitude!!!
2020-01-09 Fix CDC glitches in dds.py, finalize mag / phase calibration
    * clock domain crossing for CSR registers to the DDS controls
    was messed up / non existant. Added PulseSynchronizer.
    * Finished magnitude / phase calibration and it looks accurate!
2020-01-10 re-calibrated with 6 dB attenuators
2020-01-14 inverted status led
2020-03-05 vvm_daemon.py: add Harmonic factors, fix calibration bug
2020-07-21 update f_ref at 1 Hz, use time.time()
2020-08-18 s7_iserdes.py: add elastic buffers
    * add BUFG to sample clock to let placer use the full
    FPGA fabric (would only use one clock region before)
    * the global sample clock (BUFG) and the local clocks in
    each clockregion (BUFR) are now treated as asynchronous
    clock domains
    * add `ElasticBuffer` FIFOs to move data from local clocks to
    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
